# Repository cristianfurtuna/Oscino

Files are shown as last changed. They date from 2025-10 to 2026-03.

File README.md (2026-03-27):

# OSCINO - Osciloscop digital interfațat USB cu intrare izolată galvanic
Proiectul nostru constă într-un osciloscop digital interfațat prin USB, capabil să achiziționeze, să proceseze și să afișeze semnale electrice în timp real pe PC.
## Specificații
- in: 5V DC USB-C;<br>
- out: >2 Mbit/s serial UART data;<br>
- Arduino Mega compatible pinout
- sampling rate: ~300 ksa/s;<br>
- AC/DC coupling;<br>
- Galvanically Isolated Frontend with Differential Signal Aquisition;<br>
- 0...230V AC/DC input range using different attenuation stages;<br>
- Attenuator for High Input Voltages;<br>
- UI for PC use;<br>
- timebase and synchronisation (trigger).<br>
## Elaborare etape
- [x] Alegere componente<br>
- [x] Schemă electrică<br>
- [x] Cablaj<br>
- [x] Prototip<br>
- [x] Programare uC<br>
- [x] Programare UI<br>
- [x] Testare<br>
- [x] Elaborare documentație<br>
- [x] Realizare prezentare PowerPoint<br>
## Alegerea unui microcontroller potrivit
- [ ] C8051F120 -> preț: $11.22<br>
- [ ] STM32H743ZIT6 -> preț: $15.23<br>
- [ ] MIMXRT1062DVL6B -> preț: $12.00<br>
- [x] ATMEGA 2560 -> preț: $10.56<br>
## Asamblarea PCB-ului la fabrică este mult prea scumpă pentru a finaliza cablajul (TBD asamblare manuală)

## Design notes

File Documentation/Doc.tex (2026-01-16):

% !TeX program = lualatex
\documentclass[12pt,a4paper]{report}

% --------------------- PACKAGES ---------------------
\usepackage{fontspec}             % Custom font
\usepackage{pdfpages}             % Atach PDFs
\usepackage{graphicx}             % Images
\usepackage{amsmath,amssymb}      % Math
\usepackage{caption}              % Figure/table captions
\usepackage{subcaption}           % Subfigures
\usepackage{geometry}             % Margins
\usepackage{fancyhdr}             % Headers/footers
\usepackage{tocloft}              % ToC/List formatting
\usepackage[acronym,nonumberlist]{glossaries} % Acronyms
\usepackage[hidelinks]{hyperref}  % Hyperlinks
\usepackage{titlesec}             % Section title styling
\usepackage{listings}             % Source code
\usepackage{chngcntr}             % Counter tweaks
\usepackage{tabularx}             % Tables
\usepackage{tikz}                 % Graphs
\usepackage{pgfplots}             % Plots
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

\titleformat{\subsection}
{\normalfont\fontsize{12}{16}\bfseries\selectfont}
{\thesubsection}{16pt}{}
\titlespacing{\subsection}{1.25cm}{10pt}{0pt}

\renewcommand{\normalsize}{\fontsize{12}{16}\selectfont}

% ------- HEADER & FOOTER
\pagestyle{fancy}
\setlength{\headheight}{18pt}
\setlength{\footskip}{70pt}
\fancyhf{}
\fancyhead[L]{
	\ifodd\value{page}{\projecttitle}
	\else\makebox[0pt][l]{\parbox[b]{\headwidth}{\raggedleft{\studentname}}}
	\fi}
\fancyfoot[C]{\raisebox{15mm}{\thepage}}

\fancypagestyle{plain}{
	\fancyhf{}
	\fancyhead[L]{
		\ifodd\value{page}{\projecttitle}
		\else\makebox[0pt][l]{\parbox[b]{\headwidth}{\raggedleft{\studentname}}}
		\fi}
	\fancyfoot[C]{\raisebox{15mm}{\thepage}}
}

\fancypagestyle{plainfooter}{
	\fancyhf{}
	\renewcommand{\headrulewidth}{0pt}\setlength{\footskip}{70pt}
	\fancyfoot[C]{\raisebox{15mm}{\thepage}}
}

% --------------------- FIGURE, TABLE & CODE STYLES -----------------

% ------- TABLE OF CONTENTS
\renewcommand{\cftchapdotsep}{\cftdotsep}
\setlength{\cftchapnumwidth}{3em}
\renewcommand{\cftchapleader}{\cftdotfill{\cftchapdotsep}}
\AtBeginDocument{\renewcommand\contentsname{}}

% ------- BIBLIOGRAPHY
\defbibheading{bibliography}[\refname]{\chapter{Bibliografie}}
\renewcommand*{\bibfont}{\small}

% ------- FIGURES
\captionsetup{
	font=small,
	labelfont=bf,
	labelsep=period
}

\AtBeginDocument{
	\renewcommand{\figurename}{Figura}
	\counterwithout{figure}{chapter}
	\renewcommand{\listfigurename}{}
	\renewcommand{\cftfigpresnum}{Figura~}
	\renewcommand{\cftfigaftersnum}{.} 
	\settowidth{\cftfignumwidth}{Figură 100.} 
}

% For removing extra space in list of figures
% \makeatletter
% \def\@chapter[#1]#2{
	%   \ifnum\c@secnumdepth>\m@ne%
	%     \refstepcounter{chapter}
	%     \typeout{\@chapapp\space\thechapter.}
	%     \addcontentsline{toc}{chapter}{\protect\numberline{\thechapter}#1}
	%   \else \addcontentsline{toc}{chapter}{#1} \fi
	%   \chaptermark{#1}
	%   \addtocontents{lot}{\protect\addvspace{10\p@}}
	%   \if@twocolumn\@topnewpage[\@makechapterhead{#2}] 
	%   \else \@makechapterhead{#2} \@afterheading\fi}
% \makeatother

% ------- TABLES
\captionsetup[table]{
	justification=raggedleft,
	singlelinecheck=false
}

\AtBeginDocument{
	\counterwithout{table}{chapter}
	\renewcommand{\listtablename}{}
	\renewcommand{\cfttabpresnum}{Tabelul~}
	\renewcommand{\cfttabaftersnum}{.}
	\settowidth{\cfttabnumwidth}{Tabelul 100.}
	\renewcommand{\tablename}{Tabelul}
}

\newcolumntype{L}[1]{>{\raggedright\arraybackslash}p{#1}}
\newcolumntype{C}[1]{>{\centering\arraybackslash}m{#1}}

% For removing extra space in list of tables
% \makeatletter
% \def\@chapter[#1]#2{
	%   \ifnum\c@secnumdepth>\m@ne
	%     \refstepcounter{chapter}
	%     \typeout{\@chapapp\space\thechapter.}
	%     \addcontentsline{toc}{chapter}{\protect\numberline{\thechapter}#1}
	%   \else \addcontentsline{toc}{chapter}{#1} \fi
	%   \chaptermark{#1}
	%   \addtocontents{lot}{\protect\addvspace{0pt}}
	%   \if@twocolumn\@topnewpage[\@makechapterhead{#2}]
	%   \else\@makechapterhead{#2}\@afterheading\fi}
% \makeatother

% ------- SOURCE CODE
\lstset{
	basicstyle=\fontspec{Courier New}\fontsize{12}{9.6}\selectfont,
	numbers=left,
	numberstyle=\scriptsize,
	breaklines=true,
	captionpos=b,
	frame=none,
	showstringspaces=false,
	xleftmargin=0.6cm,
}

% --------------------- ACRONYMS ---------------------
% ------- ADD ALL ACRONYMS HERE - REFERENCE THEM IN TEXT WITH \gls{name}
\newacronym{aicors}{AICoRS}{Artificial Intelligence-enabled Hardware Cosmic Radiation Sensor for Space Applications}
\newacronym{bga}{BGA}{Ball Grid Array}
\newacronym{bram}{BRAM}{Block Random-Access Memory}
\newacronym{can}{CAN}{Controller Area Network}
\newacronym{cmos}{CMOS}{Complementary Metal–Oxide–Semiconductor}

% --------------------- DOCUMENT ---------------------
% ------- UPDATE HERE WITH CORRESPONDING VALUES - NAME & TITLE
\newcommand{\studentname}{Furtună Cristian și Iordache Denis-Ninel}
\newcommand{\projecttitle}{Osciloscop Digital cu Izolare Galvanica}

\begin{document}
	
	% ------- THIS DOCUMENT IS MADE SEPARATELY AND ADDED HERE
	% ------- NO NEED TO MODIFY HERE - JUST UNCOMMENT

	\includepdf[pages=-, pagecommand={\thispagestyle{empty}}] {Anexe/Prima pagina.pdf}

	% ------- THE FOLLOWING PAGES ARE AUTOMATED - NO NEED TO MODIFY
	\chapter*{Cuprins}
	\vspace{-8em}
	\tableofcontents
	\newpage
	
	\chapter {Specificații hardware}
	\section{Componente alese \\} 
	\section*{Integrate parte Analogică}
	\begin{itemize}
		\item AMC3330 -- Amplificator izolat de precizie, optimizat pentru masurarea tensiunii
		\item ADS8920BRGET -- Convertor Analog-Digital (ADC) tip SAR de inalta viteza
		\item THS4521IDGK -- Amplificator operational complet diferential  zgomot redus
		\item LTV-356T -- Optocuploare pentru izolarea galvanica a semnalelor
		\item REF5045AD -- Referinta de tensiune de precizie (4.5V) si deriva termica mica
		\item TS5A23159DGS -- Comutator analogic dual SPDT (Single Pole Double Throw)
		\item ADuM1401xRW -- Izolator digital cu 4 canale pentru liniile de date
	\end{itemize}
	
	\section*{Integrate Digitale si de Alimentare}
	\begin{itemize}
		\item TEA1-0505 -- Convertor DC/DC izolat de 1 Watt pentru alimentare și izolare galvanică
		\item TPS259571DSGR -- Siguranta electronica (eFuse) cu monitorizare si protectie
		\item ATMEGA2560-16AU -- Microcontroler principal pe 8 biti, familia AVR
		\item FT230XQ -- Circuit interfata punte USB la UART serial
		
	\end{itemize}
	\section{Specificații finale \\}
	
	\begin{itemize}
		\item Backwards compatibility cu Arduino IDE (maparea pinilor este realizată în stil Arduino Mega)
		\item Frecvență maximă a semnalului de măsurat circa 300kHz (în funcție de configurarea ADC-ului, limită impusă de amplificatorul de intrare)
		\item Alimentare unică prin USB-C de 5V
		\item Transfer de date prin USB-C (Max. 2Mb/s)
		\item Intrare BNC
		\item Cuplaj AC/DC
		\item Encodere digitale pentru control al afișajului (baza de timp și scară de tensiune)
		\item Tensiune semnal de intrare >230Vac
		\item Dublă izolare galvanică pe interfața de intrare a semnalelor.
		
	\end{itemize}
	
	\section{Design hardware și pcb}
	Ideea acestui proiect este să creeze o izolare galvanică între partea analogică și digitală și să măsoare diferențial tensiunile aplicate la intrare astfel încât să protejeze echipamentul cu care 
	
	\begin{figure}[h!]
		\centering
		
		\caption{Schema etajului de intrare.}%
		\label{fig:Intrare}
	\end{figure}
	
	\begin{figure}[h!]
		\centering
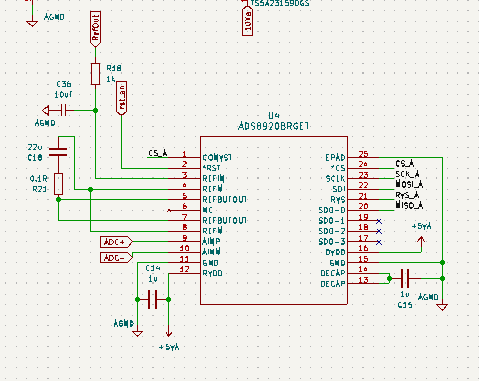
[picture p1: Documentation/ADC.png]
		
		\caption{Schema modulului ADC.}%
		\label{fig:ADC}
	\end{figure}
	
	\begin{figure}[h!]
		\centering
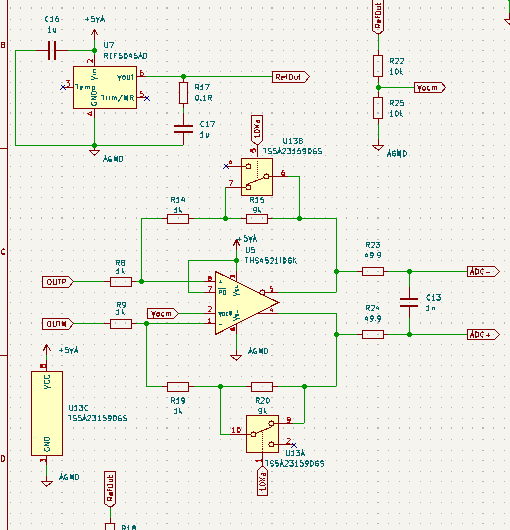
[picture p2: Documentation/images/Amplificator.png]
		
		\caption{Schema circuitului amplificator.}%
		\label{fig:Amplificator}
	\end{figure}
	
	\begin{figure}[h!]
		\centering
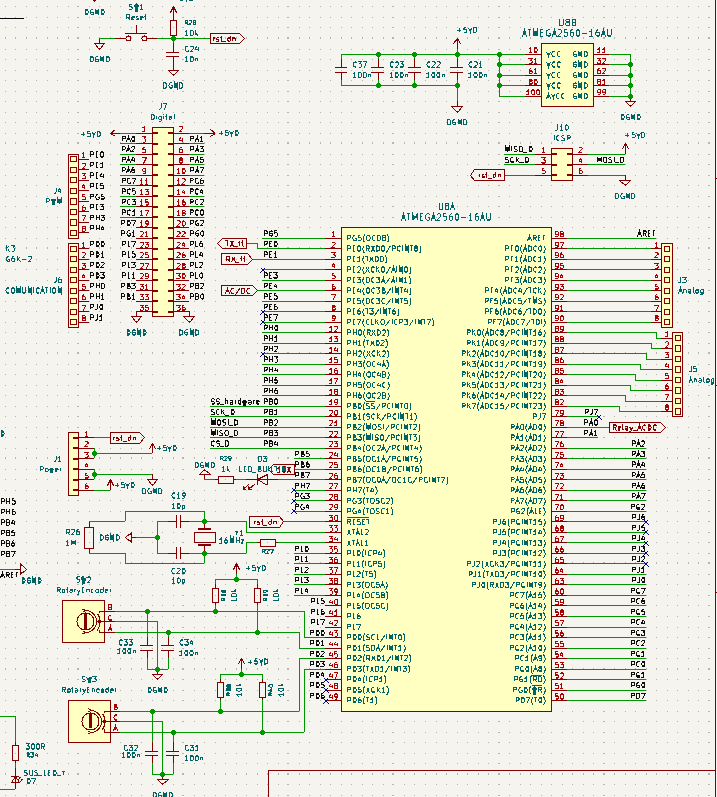
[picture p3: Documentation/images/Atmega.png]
		
		\caption{Configurația microcontrolerului ATmega.}%
		\label{fig:Atmega}
	\end{figure}

	\begin{figure}[h!]
		\centering
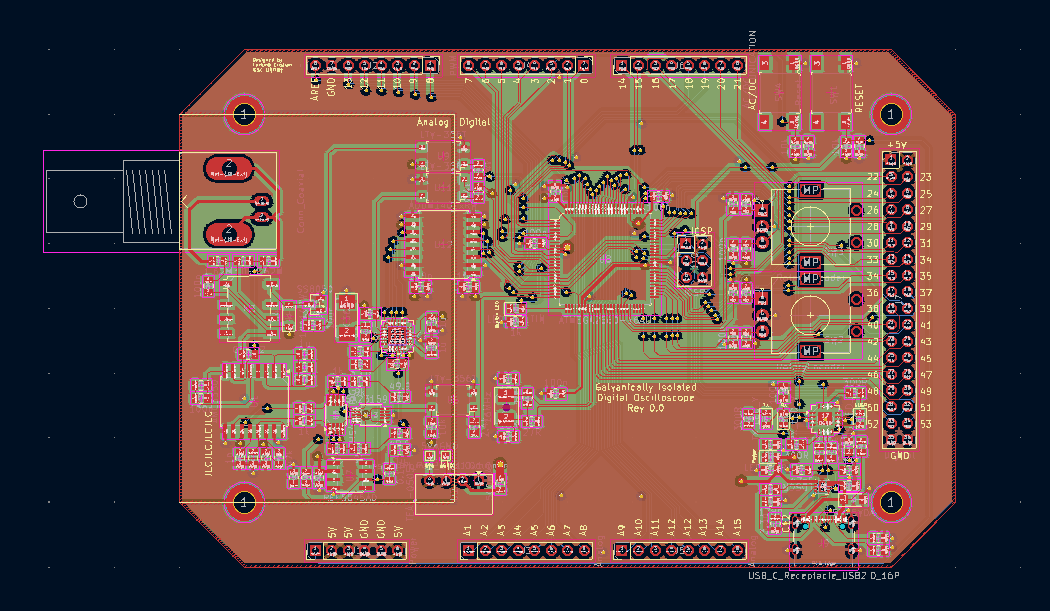
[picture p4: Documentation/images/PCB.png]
		
		\caption{Design-ul (layout-ul) plăcii PCB.}%
		\label{fig:PCB}
	\end{figure}

	\begin{figure}[h!]
		\centering
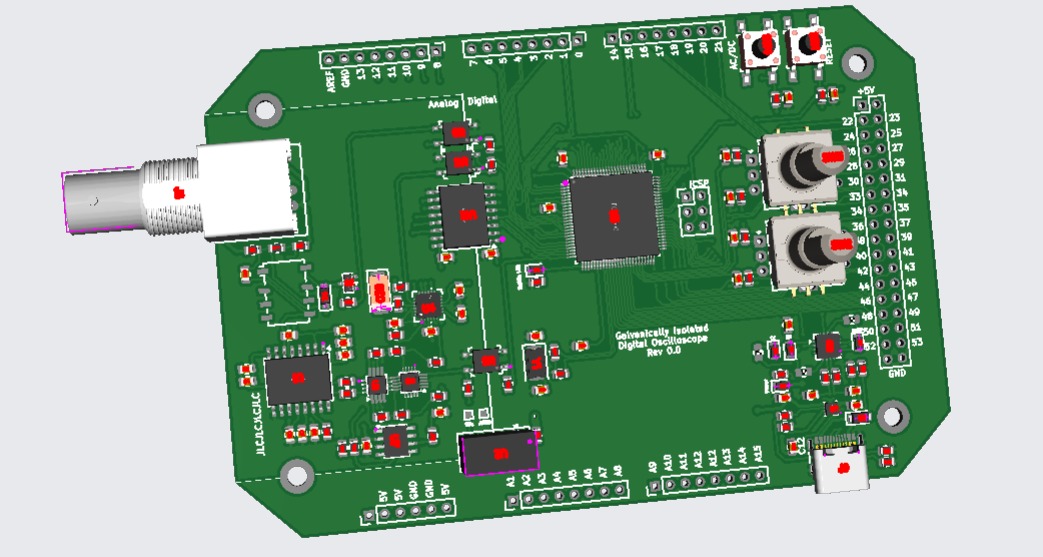
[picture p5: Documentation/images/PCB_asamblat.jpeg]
		
		\caption{Fotografie cu modulul PCB asamblat.}%
		\label{fig:PCB_asamblat}
	\end{figure}

	\section{Analiză economică}
	
	\begin{table}[h!]
		\begin{tabular}{|l|l|l|l|l|}
			\hline
			Cost PCB        & Cost PCBA                     & Cost estimativ componente & Cost estimativ minim & Cost prototip \\ 
			\hline
			$\sim$320 RON& $\sim$1300 RON & 300 + RON & 600 RON & 180 RON\\
			\hline

		\end{tabular}
	\end{table}
	
	Prin urmare, analizând cu atenție costurile din ofertele studiate, am decis să ne limităm la un PCB neasamblat + prototip realizat cu Arduino Mega 2560. Ne-am fi dorit să ne putem permite costul total de realizare a unui PCBA, dar cu măsurile de austeritate în vigoare, bursele tăiate pe perioada de vacanță și un trai tot mai scump de la o zi la alta, plus costurile de realizare a proiectului de licență, am considerat să ne oprim la o sumă totală de aprox. 500 de lei.
	
	\chapter {Specificații software}
	\section {Prototip}
	
	Așa cum a fost menționat și în secțiunea de \textbf{Analiză Economică}, pentru partea de simulare ne-am limitat la un prototip realizat cu o placă de dezvoltare Arduino Mega 2560.
	
	\begin{figure}[h!]
		\centering
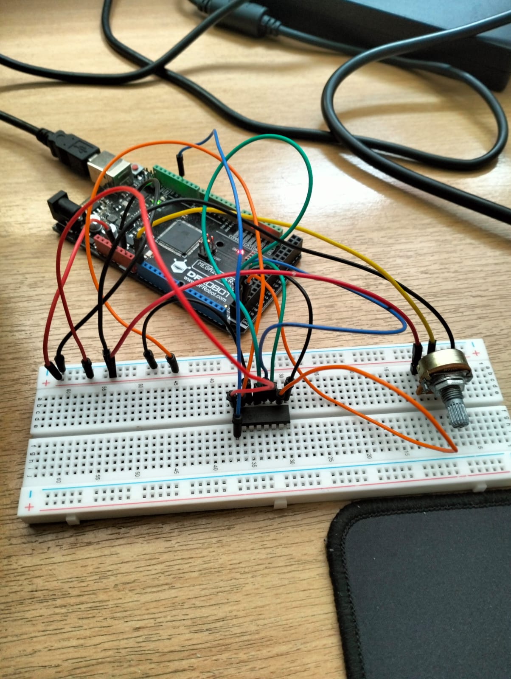
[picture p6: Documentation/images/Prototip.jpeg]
		
		\caption{Fotografie cu circuitul aferent prototipului nostru implementat pe un breadboard.}%
		\label{fig:Prototip}
	\end{figure}
	
	Pentru circuit a fost utilizat un ADC extern pe 10 biți, MCP3008 și un potențiometru pentru setarea factorului de umplere al unui semnal dreptunghiular generat pe pinul D11 al plăcii Arduino Mega 2560.
	
	Pinout-ul este evidențiat în următorul tabel:
	\begin{table}[h!]
		\centering
		\begin{tabular}{|c|c|c|}
			\hline
			Pin MCP3008        & Pin ATMEGA2560                     & Nume pini \\ 
			\hline
			1 & D11 & CH0-D11 \\
			\hline
			9 & DGND & DGND - DGND \\
			\hline
			10 & D53 & CS-SS \\
			\hline
			11 & D51 & DIN-MOSI \\
			\hline
			12 & D50 & DOUT-MISO \\
			\hline
			13 & D52 & CLK-SCK \\
			\hline
			14 & AGND & AGND-AGND \\
			\hline
			15 & 5V & VREF-5V \\
			\hline
			16 & 5V & VDD-5V \\
			\hline
		\end{tabular}
	\end{table}
	
	\section{Codul sursă utilizat}
	
	\begin{lstlisting}[language=C]
	#ifndef SPI_H
	#define SPI_H
	
	#include <avr/io.h>
	
	void SPI_MasterInit(void);
	uint8_t SPI_MasterTransmit(uint8_t data);
	void SPI_SlaveInit(void);
	uint8_t SPI_SlaveReceive(void);
	uint8_t SPI_Read_MCP3008_8bit(uint8_t channel);
	
	#endif
	\end{lstlisting}

	\begin{lstlisting}[language=C]
	#include <stdio.h>
	#include <avr/io.h>
	#include "spi.h"
	#include "uart.h"
	
	void SPI_MasterInit(void)
	{
		// Set MOSI, SS and SCK output, all others input
		DDRB |= (1 << PB2) | (1 << PB1) | (1 << PB0); // MOSI - PB2, SCK - PB1
		// Enable SPI, Master, set clock rate fck/16 (was 1 << SPR0)
		PORTB |= (1 << PB0);                           // Keep board in Master mode
		SPCR = (1 << SPE) | (1 << MSTR) | (1 << SPR0); // SPCR - SPI control register
		SPSR |= (1 << SPI2X);
	}
	
	uint8_t SPI_MasterTransmit(uint8_t data)
	{
		// Start transmission; load byte into data register
		SPDR = data; // SPDR - SPI data register
		// Wait for transmission to complete
		while (!(SPSR & (1 << SPIF)))
		;        // SPSR - SPI status register ; SPIF - SPI Interrupt Flag
		return SPDR; // read received byte after transmission
	}
	
	void SPI_SlaveInit(void)
	{
		// SET MISO output, all others input
		DDRB |= (1 << PB3); // MISO - PB3
		// Enable SPI
		SPCR = (1 << SPE); // SPCR - SPI control register
	}
	
	uint8_t SPI_SlaveReceive(void)
	{
		// Wait for reception complete
		while (!(SPSR & (1 << SPIF)))
		;        // SPSR - SPI status register ; SPIF - SPI Interrupt Flag
		return SPDR; // SPDR - SPI data register
	}
	
	// Read data from ADC
	uint8_t SPI_Read_MCP3008_8bit(uint8_t channel)
	{
		// CS Low
		PORTB &= ~(1 << PB0);
		
		// Send Start Bit (0x01)
		SPDR = 0x01;
		while (!(SPSR & (1 << SPIF)))
		;
		
		// Send config bit and select channel
		SPDR = 0x80 | (channel << 4);
		while (!(SPSR & (1 << SPIF)))
		;
		uint8_t high = SPDR;
		
		// Send dummy bit
		SPDR = 0x00;
		while (!(SPSR & (1 << SPIF)))
		;
		uint8_t low = SPDR;
		
		// CS High
		PORTB |= (1 << PB0);
		
		// Concatenam high si low
		uint16_t result = ((high & 0x03) << 8) | low;
		// Shiftare la dreapta pentru a pastra doar 1 byte
		// La frecvente mari, de regula ultimii 2 biti sunt zgomotosi
		return (uint8_t)(result >> 2);
	}
	\end{lstlisting}
	
	\begin{lstlisting}[language=C]
		#define BAUD 2000000UL // desired BAUD rate
		
		#include <avr/io.h>
		#include <avr/interrupt.h>
		#include <util/delay.h>
		#include <stdio.h>
		#include <stdint.h>
		#include "uart.h"
		#include "gpio.h"
		#include "avr/portpins.h"
		#include "pwm.h"
		#include "avr/sleep.h"
		#include "millis.h"
		#include "adc.h"
		#include "spi.h"
		
		#define PWM_FREQ 200 // Hz
		#define BATCH_SIZE 600
		
		volatile uint8_t button_pressed = 1;
		
		int main(void)
		{
			
			GPIO_set_output(ONBOARD_LED); // onboard LED
			GPIO_set_output(D11);		  // D11 as output
			
			uart_init(MYUBRR);
			SPI_MasterInit();
			millis_init();
			
			// Generate a square signal on pin D11
			PWM_init();
			PWM_attach(D11);
			ADC_init(ADC_REF_AVCC, ADC_PRESCALER_128);
			
			set_sleep_mode(SLEEP_MODE_IDLE); // Set sleep mode to power down
			
			EICRA |= (1 << ISC00); // Any logical change on INT0 generates interrupt
			EIMSK |= (1 << INT0);  // Enable INT0
			sei();				   // Enable global interrupts
			
			while (1)
			{
				// Modify duty cycle of pwm with a potentiometer
				static uint32_t last_pwm_update = 0;
				
				if (millis_now() - last_pwm_update >= 50)
				{
					uint16_t pot = ADC_read_pin(A0); // 0–1023
					uint32_t duty = (uint32_t)pot * PWM_get_max(D11) / 1023;
					
					PWM_write_raw(D11, duty); // hardware PWM
					last_pwm_update = millis_now();
				}
				
				cli(); // clear interrupts for full focus on sending ADC data
				// Send batch sync bytes 0xAA start byte, 0x55 stop byte, useful for python script
				while (!(UCSR0A & (1 << UDRE0)))
				;
				UDR0 = 0xAA;
				while (!(UCSR0A & (1 << UDRE0)))
				;
				UDR0 = 0x55;
				
				// Sending BATCH_SIZE = 600 bytes; total number of bits sent = estimated 6000 bits per for
				// Adding the start and stop bits to a byte -> 10 bits per batch
				// 6020 if we take into consideration the sync bytes for a batch
				for (uint16_t i = 0; i < BATCH_SIZE; i++)
				{
					// Read channel 0 from ADC
					uint8_t val = SPI_Read_MCP3008_8bit(0);
					
					// Send byte through UART
					while (!(UCSR0A & (1 << UDRE0)))
					;		// Wait for buffer to empty
					UDR0 = val; // Send the data
				}
				
				sei(); // enable interrupts
				_delay_us(100);
			}
		}
	\end{lstlisting}
	
	\begin{lstlisting}[language=Python]
		import sys
		import time
		import serial
		import numpy as np
		from numpy.lib.stride_tricks import sliding_window_view
		from PyQt5.QtWidgets import (
		QApplication, QMainWindow, QWidget, QVBoxLayout, QHBoxLayout,
		QLabel, QLineEdit, QPushButton, QDial, QGridLayout, QFrame, QGroupBox
		)
		from PyQt5.QtCore import QThread, pyqtSignal, Qt
		import pyqtgraph as pg
		
		# Constants
		SYNC_SEQ = b"\xAA\x55" # Sync bytes
		BATCH_SIZE = 600 # Size of ADC data batch
		ADC_REF_VOLTAGE = 5.0  # Reference voltage of ADC = VDD (5V)
		
		# Step values for volts/div and timescale
		TIME_STEPS = [0.0001, 0.0002, 0.0005, 0.001, 0.002, 0.005, 0.010, 0.020, 0.050, 0.100]
		VOLT_STEPS = [0.1, 0.2, 0.5, 1.0, 2.0, 5.0]
		
		class SerialADCReader:
		# Configure port, baud rate and timeout
		def __init__(self, port="COM5", baudrate=2000000):
		self.ser = serial.Serial(port, baudrate, timeout=0.01)
		self.rx_buf = bytearray() # Internal buffer for received data
		
		# Open the port
		def connect(self):
		if not self.ser.is_open:
		self.ser.open()
		self.ser.reset_input_buffer() # Reset internal buffer to get rid of junk data from previous runs
		
		# Close the port
		def disconnect(self):
		if self.ser.is_open:
		self.ser.close()
		
		def read_frame(self):
		# Read everything on the serial buffer
		if self.ser.in_waiting > 0:
		data = self.ser.read(self.ser.in_waiting)
		self.rx_buf.extend(data) # Add everything from the serial buffer into our internal buffer for further processing
		
		frames_found = []
		while True:
		# Search the buffer for Sync bits to find a batch
		idx = self.rx_buf.find(SYNC_SEQ)
		# If there are no Sync bits found and the buffer has grown in size too much
		# Clear the buffer and keep only the last 100 bytes
		if idx == -1:
		if len(self.rx_buf) > 2 * BATCH_SIZE:
		self.rx_buf = self.rx_buf[-100:] 
		break
		
		# Verify if there are enough bytes for a full batch
		# If there are not, wait for full batch
		pkt_len = 2 + BATCH_SIZE # 2 bytes Sync + batch size
		if len(self.rx_buf) < idx + pkt_len:
		break 
		
		payload = self.rx_buf[idx + 2 : idx + pkt_len] # Skip sync bytes and extract only the necessary data
		raw_data = np.frombuffer(payload, dtype=np.uint8) # Convert into decimal values (0-255 for 8 bits)
		# Scale the values into (0 - 1020) to simulate 10 bit ADC
		# Added so I don't have to modify my program (previously used to send all 10 bits of ADC data)
		scaled_data = raw_data.astype(np.int16) * 4
		frames_found.extend(scaled_data)
		del self.rx_buf[:idx + pkt_len]
		
		return frames_found if frames_found else None
		
		# Preluare date din interfata seriala pe un thread separat, fara sa blochez GUI-ul
		class SerialThread(QThread):
		samples_ready = pyqtSignal(object) # Anunta programul principal ca am citit un batch pentru display
		
		# Initializare citire buffer serial
		def __init__(self, port):
		super().__init__()
		self.port = port
		self.running = False
		self.reader = None
		
		def run(self):
		try:
		self.reader = SerialADCReader(self.port)
		self.reader.connect()
		self.running = True
		#In timp ce citesc datele, daca am un frame complet, il trimit catre programul principal pentru prelucrare
		while self.running:
		samples = self.reader.read_frame()
		if samples:
		self.samples_ready.emit(samples)
		else:
		self.msleep(1) # Mic delay daca inca nu au aparut date ca sa nu blocam thread-ul inutil
		except Exception as e:
		print(f"Serial Error: {e}")  #In caz de eroare pe serial read
		finally:
		if self.reader:
		self.reader.disconnect() # Inchidere port serial (cu sau fara eroare)
		
		def stop(self):
		self.running = False
		self.wait()
		
		class MainWindow(QMainWindow):
		def __init__(self):
		super().__init__()
		
		self.serial_thread = None
		
		# Buffer circular
		self.capture_buffer = []
		self.MAX_CAPTURE = 500000 # Buffer mare
		
		# Variabile interne
		self.measured_sps = 60000.0 # Valoare default pana la masura
		self.total_samples_received = 0
		self.last_time_check = time.time()
		
		# Scope state
		self.time_idx = 4   # Default 2ms (index 4 in TIME_STEPS)
		self.volt_idx = 3   # Default 1V (index 3 in VOLT_STEPS)
		self.trigger_lvl = 2.5
		self.vert_offset = 0.0
		
		self.last_draw_time = 0
		self.FPS_LIMIT = 30  
		self.last_valid_frame = None 
		self.trigger_lost_timer = 0
		
		self._setup_ui()
		self._setup_plot()
		self.update_scope_settings() # Apply initial settings
		
		def _setup_ui(self):
		# Styling dial buttons
		dial_style = """
		QDial { background-color: #333; }
		"""
		
		# Zona de conectare
		self.port_input = QLineEdit("COM5") 
		self.port_input.setFixedWidth(80)
		self.btn_connect = QPushButton("ON")
		self.btn_connect.setCheckable(True)
		self.btn_connect.clicked.connect(self.toggle_connection)
		self.btn_connect.setStyleSheet("QPushButton { background-color: #444; color: white; border-radius: 5px; font-weight: bold; } QPushButton:checked { background-color: #00E676; color: black; }")
		self.btn_connect.setFixedSize(50, 50)
		
		conn_group = QGroupBox("Input")
		conn_layout = QVBoxLayout()
		conn_layout.addWidget(QLabel("PORT"))
		conn_layout.addWidget(self.port_input)
		conn_layout.addWidget(self.btn_connect)
		conn_layout.addStretch()
		conn_group.setLayout(conn_layout)
		
		# Zona Verticala (Volts/Div & Position - offset)
		self.dial_volts = QDial()
		self.dial_volts.setRange(0, len(VOLT_STEPS)-1)
		self.dial_volts.setValue(self.volt_idx)
		self.dial_volts.setNotchesVisible(True)
		self.dial_volts.valueChanged.connect(self.update_scope_settings)
		self.lbl_volts = QLabel("1 V")
		self.lbl_volts.setAlignment(Qt.AlignCenter)
		
		self.dial_offset = QDial()
		self.dial_offset.setRange(-60, 60) # +/- 6.0 Diviziuni
		self.dial_offset.setValue(0)
		self.dial_offset.setNotchesVisible(True)
		self.dial_offset.valueChanged.connect(self.update_scope_settings)
		self.lbl_offset = QLabel("Pos: 0 Div")
		self.lbl_offset.setAlignment(Qt.AlignCenter)
		
		vert_group = QGroupBox("Vertical")
		vert_layout = QVBoxLayout()
		vert_layout.addWidget(QLabel("SCALE"))
		vert_layout.addWidget(self.dial_volts)
		vert_layout.addWidget(self.lbl_volts)
		vert_layout.addWidget(QLabel("POSITION"))
		vert_layout.addWidget(self.dial_offset)
		vert_layout.addWidget(self.lbl_offset)
		vert_group.setLayout(vert_layout)
		
		# Zona Orizontală (Time/Div)
		self.dial_time = QDial()
		self.dial_time.setRange(0, len(TIME_STEPS)-1)
		self.dial_time.setValue(self.time_idx)
		self.dial_time.setNotchesVisible(True)
		self.dial_time.valueChanged.connect(self.update_scope_settings)
		self.lbl_time = QLabel("2 ms")
		self.lbl_time.setAlignment(Qt.AlignCenter)
		
		horiz_group = QGroupBox("Horizontal")
		horiz_layout = QVBoxLayout()
		horiz_layout.addWidget(QLabel("TIME/DIV"))
		horiz_layout.addWidget(self.dial_time)
		horiz_layout.addWidget(self.lbl_time)
		horiz_layout.addStretch()
		horiz_group.setLayout(horiz_layout)
		
		# Zona Trigger
		self.dial_trig = QDial()
		self.dial_trig.setRange(0, 50) # 0.0 la 5.0V
		self.dial_trig.setValue(25)
		self.dial_trig.setNotchesVisible(True)
		self.dial_trig.valueChanged.connect(self.update_scope_settings)
		self.lbl_trig_val = QLabel("T: 2.5V")
		self.lbl_trig_val.setAlignment(Qt.AlignCenter)
		
		self.lbl_trig_status = QLabel("NO SIG")
		self.lbl_trig_status.setStyleSheet("color: gray; font-weight: bold; border: 1px solid gray; padding: 2px;")
		self.lbl_trig_status.setAlignment(Qt.AlignCenter)
		
		trig_group = QGroupBox("Trigger")
		trig_layout = QVBoxLayout()
		trig_layout.addWidget(QLabel("LEVEL"))
		trig_layout.addWidget(self.dial_trig)
		trig_layout.addWidget(self.lbl_trig_val)
		trig_layout.addWidget(self.lbl_trig_status)
		trig_group.setLayout(trig_layout)
		
		# Panou Control (stanga)
		ctrl_layout = QVBoxLayout()
		ctrl_layout.addWidget(conn_group)
		ctrl_layout.addWidget(vert_group)
		ctrl_layout.addWidget(horiz_group)
		ctrl_layout.addWidget(trig_group)
		ctrl_layout.addStretch()
		
		ctrl_widget = QWidget()
		ctrl_widget.setLayout(ctrl_layout)
		ctrl_widget.setFixedWidth(180) # Latime fixa a panoului
		
		# Plot Area
		self.plot_widget = pg.GraphicsLayoutWidget()
		self.plot_widget.setBackground('#111') # Background inchis
		self.plot = self.plot_widget.addPlot(title="NIBIRUSCOPE")
		self.curve = self.plot.plot(pen=pg.mkPen('#00E676', width=2)) 
		
		# Setup Grid
		self.plot.showGrid(x=True, y=True, alpha=0.3)
		self.plot.setLabel('bottom', 'Time', units='s')
		self.plot.setLabel('left', 'Voltage', units='V')
		
		# Main Layout
		main_layout = QHBoxLayout()
		main_layout.addWidget(ctrl_widget)
		main_layout.addWidget(self.plot_widget)
		
		container = QWidget()
		container.setLayout(main_layout)
		self.setCentralWidget(container)
		self.setWindowTitle("NibiruScope")
		self.resize(1200, 700)
		
		def _setup_plot(self):
		pg.setConfigOptions(antialias=False) 
		
		def update_scope_settings(self):
		# Timebase
		idx_t = self.dial_time.value()
		time_val = TIME_STEPS[idx_t]
		
		if time_val < 0.001:
		self.lbl_time.setText(f"{time_val*1000000:.0f} µs")
		elif time_val < 1.0:
		self.lbl_time.setText(f"{time_val*1000:.0f} ms")
		else:
		self.lbl_time.setText(f"{time_val:.2f} s")
		
		# Volts/div
		idx_v = self.dial_volts.value()
		volt_per_div = VOLT_STEPS[idx_v]
		self.lbl_volts.setText(f"{volt_per_div} V")
		
		# Position - Offset
		# Modifica valoarea dial-ului in diviziuni
		offset_in_divs = self.dial_offset.value() / 10.0
		
		# Scalare pentru diferite valori de volts/div
		self.vert_offset = offset_in_divs * volt_per_div 
		
		# Afisare label offset scalat in volti pentru dial
		self.lbl_offset.setText(f"Pos: {self.vert_offset:+.1f}V")
		
		# Trigger
		trig_raw = self.dial_trig.value()
		self.trigger_lvl = trig_raw / 10.0
		self.lbl_trig_val.setText(f"T: {self.trigger_lvl:.1f}V")

		# Axa X
		self.plot.setXRange(0, time_val * 10, padding=0)
		
		# Axa Y:
		half_screen_volts = volt_per_div * 4 
		self.plot.setYRange(-half_screen_volts, half_screen_volts, padding=0)
		
		# Functionalitate on/off
		def toggle_connection(self):
		if self.btn_connect.isChecked():
		port = self.port_input.text()
		self.serial_thread = SerialThread(port)
		self.serial_thread.samples_ready.connect(self.process_data)
		self.serial_thread.start()
		self.btn_connect.setText("OFF")
		else:
		if self.serial_thread:
		self.serial_thread.stop()
		self.serial_thread = None
		self.btn_connect.setText("ON")
		
		def process_data(self, samples):
		self.total_samples_received += len(samples)
		now = time.time()
		if now - self.last_time_check >= 1.0:
		self.measured_sps = self.total_samples_received / (now - self.last_time_check)
		self.total_samples_received = 0
		self.last_time_check = now
		# Actualizăm titlul ferestrei
		# self.plot.setTitle(f"NIBIRU SCOPE - Sampling: {self.measured_sps/1000:.1f} kSPS")
		
		# Buffer Management
		self.capture_buffer.extend(samples)
		if len(self.capture_buffer) > self.MAX_CAPTURE:
		self.capture_buffer = self.capture_buffer[-self.MAX_CAPTURE:]
		
		# Limitare FPS
		if now - self.last_draw_time < (1.0 / self.FPS_LIMIT):
		return

		time_per_div = TIME_STEPS[self.dial_time.value()]
		total_time_screen = time_per_div * 10
		
		n_display_points = int(total_time_screen * self.measured_sps)
		
		n_display_points = max(10, min(n_display_points, len(self.capture_buffer)))
		
		if len(self.capture_buffer) < n_display_points * 2:
		return
		
		# Procesare date
		# Luăm un chunk mare din coadă pentru a căuta trigger-ul
		# Luăm dublu cât ne trebuie ca să avem loc de manevră
		search_window = int(n_display_points * 2.5) 
		if search_window > len(self.capture_buffer):
		search_window = len(self.capture_buffer)
		
		raw_data = np.array(self.capture_buffer[-search_window:], dtype=np.int16)
		
		# Filtru Median (doar dacă avem destule puncte)
		if len(raw_data) > 5:
		window = sliding_window_view(raw_data, window_shape=3)
		filtered_data = np.median(window, axis=1)
		else:
		filtered_data = raw_data
		
		# --- 6. TRIGGER LOGIC ---
		trig_adc = int((self.trigger_lvl / 5.0) * 1023)
		
		# Cautare rising edge
		binary = (filtered_data >= trig_adc).astype(np.int8)
		edges = np.diff(binary)
		trigger_indices = np.where(edges == 1)[0]
		
		frame_to_draw = None
		found_trigger = False
		
		if len(trigger_indices) > 0:
		
		for idx in reversed(trigger_indices):
		if idx + n_display_points < len(filtered_data):
		if np.all(filtered_data[idx+1 : idx+4] > (trig_adc - 20)):
		frame_to_draw = filtered_data[idx : idx + n_display_points]
		found_trigger = True
		
		self.lbl_trig_status.setText("LOCKED")
		self.lbl_trig_status.setStyleSheet("color: #00E676; border: 1px solid #00E676; font-weight: bold;")
		self.trigger_lost_timer = now
		break
		
		# Auto roll
		if not found_trigger:
		if now - self.trigger_lost_timer > 0.3: 
		self.lbl_trig_status.setText("AUTO")
		self.lbl_trig_status.setStyleSheet("color: orange; border: 1px solid orange;")
		# Luam ultimele date disponibile
		if len(filtered_data) >= n_display_points:
		frame_to_draw = filtered_data[-n_display_points:]
		
		# Desenare
		if frame_to_draw is not None:
		self.last_draw_time = now
		
		# Conversie in Volti
		real_volts = (frame_to_draw / 1023.0) * 5.0
		
		display_volts = (real_volts - 2.5) + self.vert_offset
		
		# Generare axa timp
		total_time_screen = time_per_div * 10
		t = np.linspace(0, total_time_screen, len(display_volts))
		
		self.curve.setData(t, display_volts)
		
		if __name__ == "__main__":
		app = QApplication(sys.argv)
		window = MainWindow()
		window.show()
		sys.exit(app.exec_())
	\end{lstlisting}

	% ------- THESE DOCUMENTS ARE MADE SEPARATELY AND ADDED HERE
	% ------- NO NEED TO MODIFY HERE - JUST UNCOMMENT
	% \newpage
	% \addcontentsline{toc}{chapter}{Anexa 1}
	% \includepdf[pages=-, pagecommand={\thispagestyle{plainfooter}}]
	% {Anexe/Anexa 1.pdf}
	
	% \newpage
	% \addcontentsline{toc}{chapter}{Anexa 2} 
	% \includepdf[pages=-, pagecommand={\thispagestyle{plainfooter}}]
	% {Anexe/Anexa 2.pdf}
	
	% \newpage
	% \addcontentsline{toc}{chapter}{Anexa 3}
	% \includepdf[pages=-, pagecommand={\thispagestyle{plainfooter}}]
	% {Anexe/Anexa 3.pdf}
	
	% \newpage
	% \addcontentsline{toc}{chapter}{Declarație privind originalitatea}
	% \includepdf[pages=-, pagecommand={\thispagestyle{plainfooter}}]
	% {Anexe/Declaratie originalitate.pdf}
	
\end{document}

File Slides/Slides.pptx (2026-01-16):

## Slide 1

NIBIRU
Osciloscop Digital cu Izolație Galvanică

Furtună Cristian
Iordache Denis-Ninel

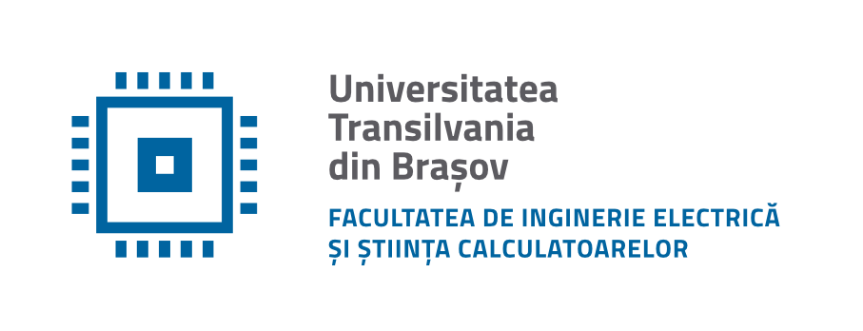
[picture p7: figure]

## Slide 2

Schematic

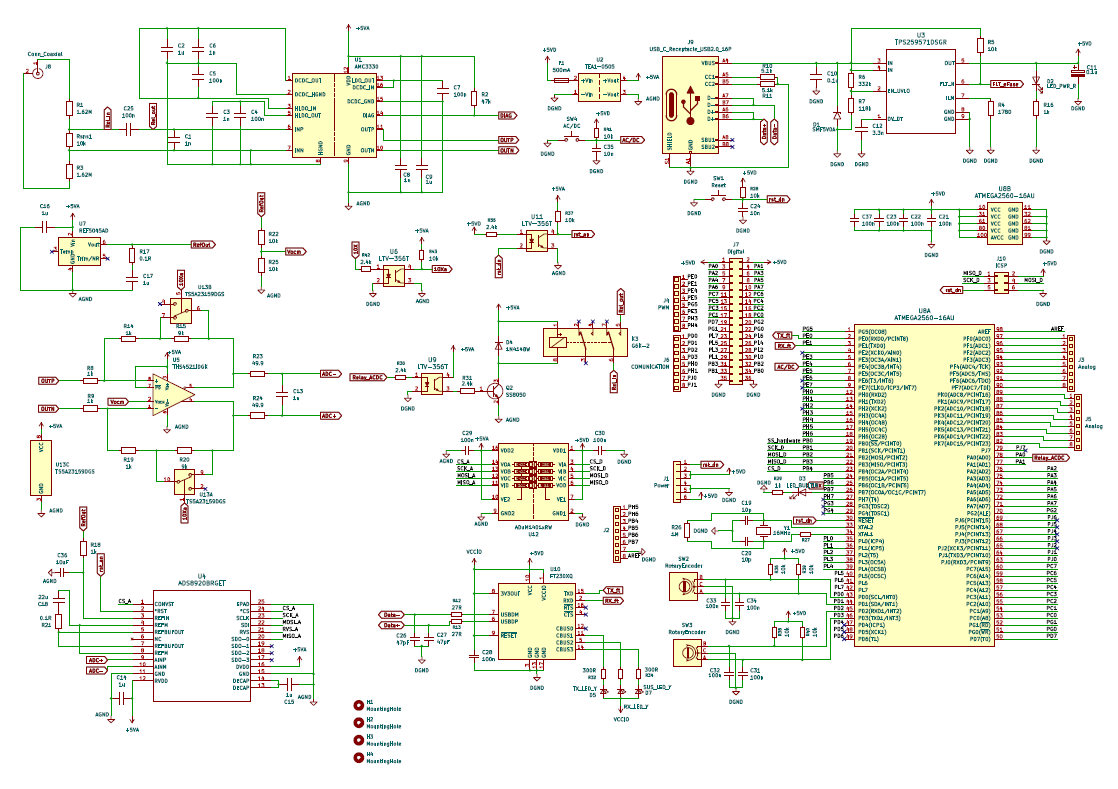
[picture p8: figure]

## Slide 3

PCB Design

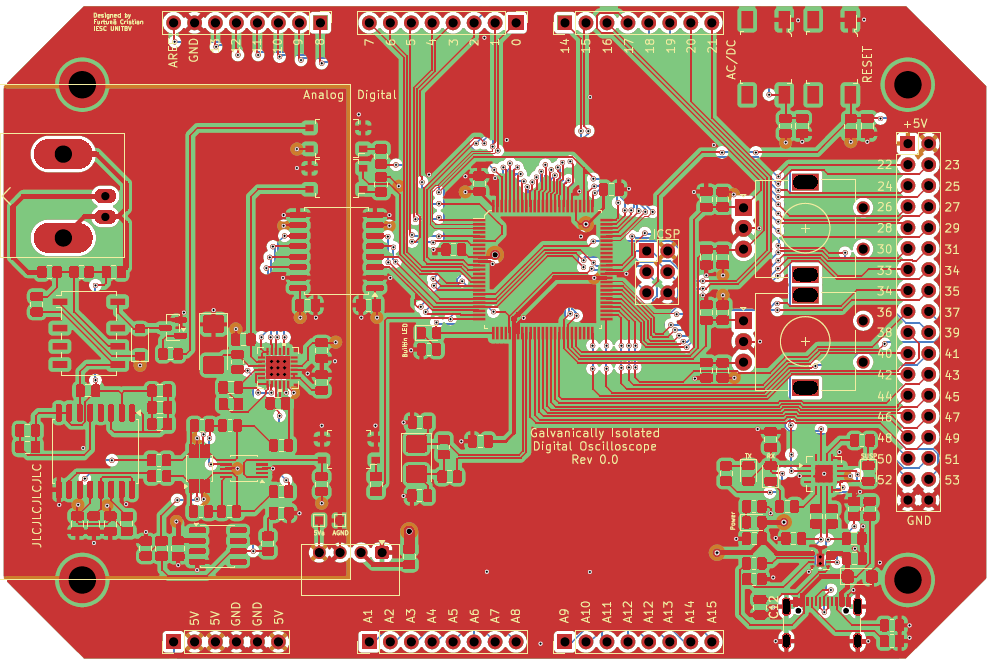
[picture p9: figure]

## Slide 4

PCB Design Bottom

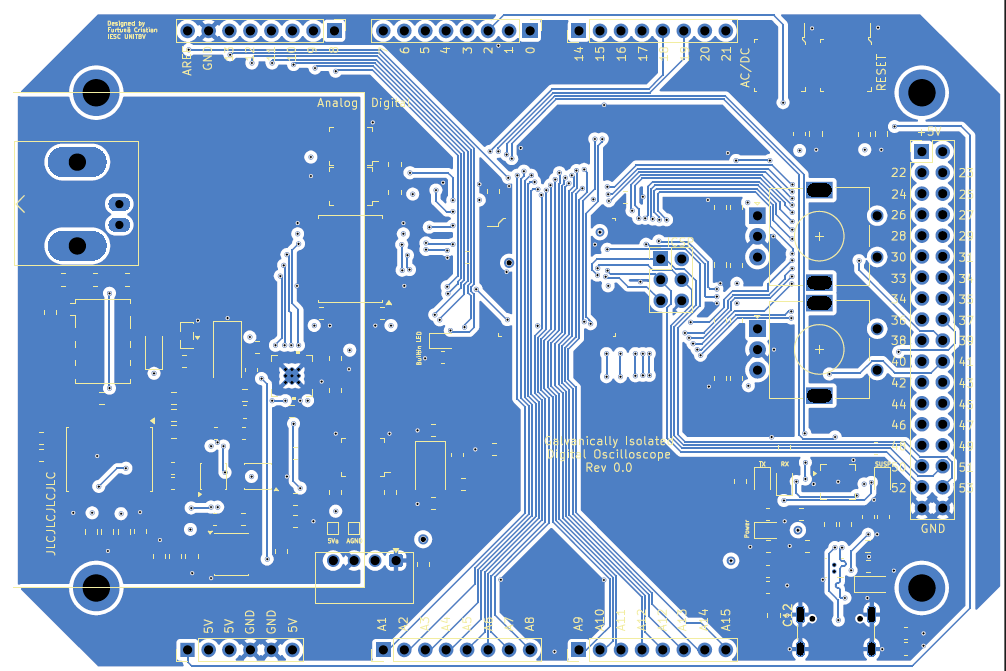
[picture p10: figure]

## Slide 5

PCB Design 3D

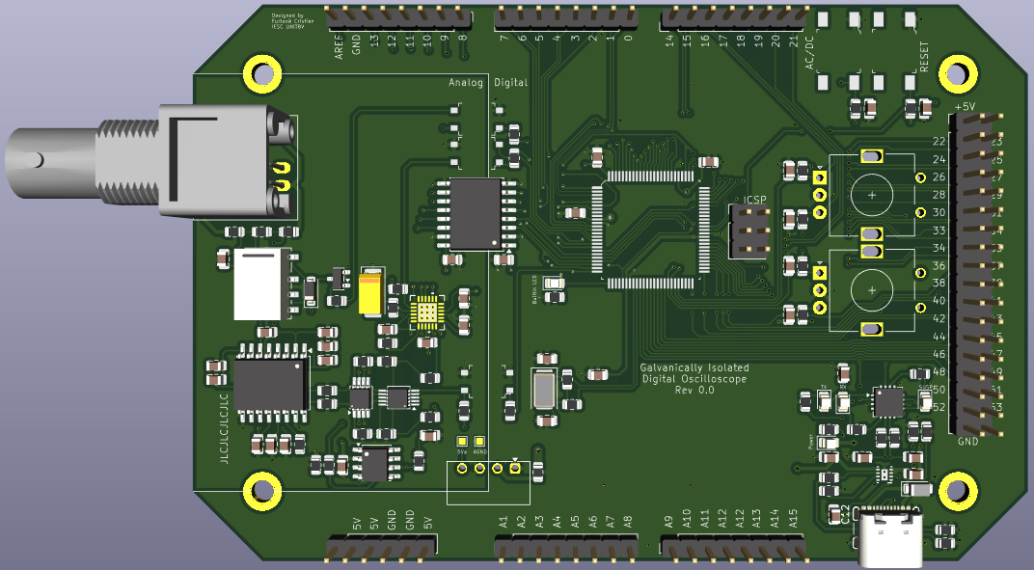
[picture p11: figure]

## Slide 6

Specificații hardware finale

• Backwards compatibility cu Arduino IDE (maparea pinilor este realizată în stil Arduino Mega)
• Frecvență maximă a semnalului de măsurat circa 300kHz (în funcție de configurarea ADC-ului, limită impusă de amplificatorul de intrare)
• Alimentare unică prin USB-C de 5V
• Transfer de date prin USB-C (Max. 2Mb/s)
• Intrare BNC
• Cuplaj AC/DC
• Encodere digitale pentru control al afișajului (baza de timp și scară de tensiune)

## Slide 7

Specificații hardware finale

• Modularitate hardware și software, posibilitatea de reconfigurare a oricărui parametru și de adăugare a unor funcționalități noi prin pinii GPIO
• Consum energetic estimativ maxim mai mic de 2W
• Circuit de protecție la scurtcircuit la alimentare (e-Fuse)
• Comunicație digitală izolată prin izolatori cu cuplaj inductiv și optocuploare
• ADC cu aproximări succesive configurabil

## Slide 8

Specificații software

• Prototip realizat cu placă de dezvoltare Arduino Mega 2560 și ADC extern pe 10 biți MCP3008.
• Comunicare cu ADC-ul extern realizată prin SPI.
• Trimitere date seriale prin UART pentru afișare pe GUI realizat în Python.
• Semnal de test PWM cu duty cycle configurabil generat cu Arduino Mega 2560.
• GUI similar unui osciloscop real, funcționalități de trigger, modificare volt/div (SCALE), modificare timebase, poziționare semnal pe ecran.

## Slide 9

GUI Demo

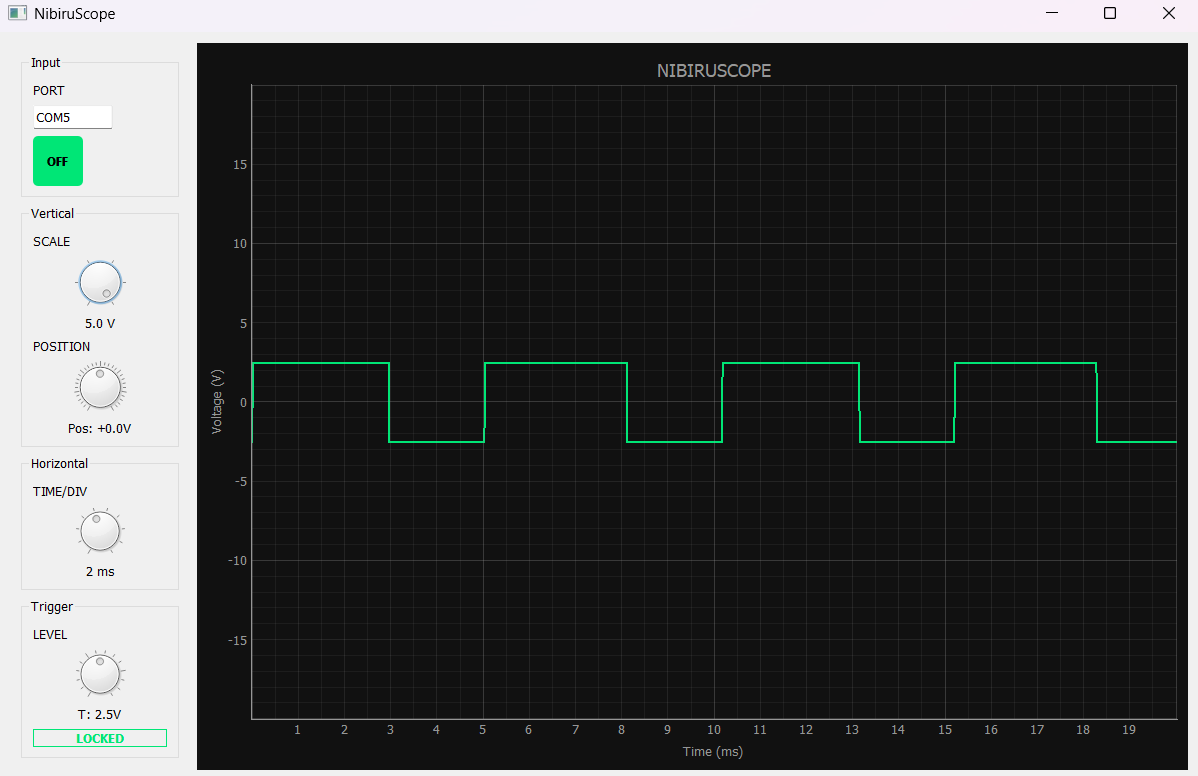
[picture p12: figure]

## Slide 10

GUI Demo

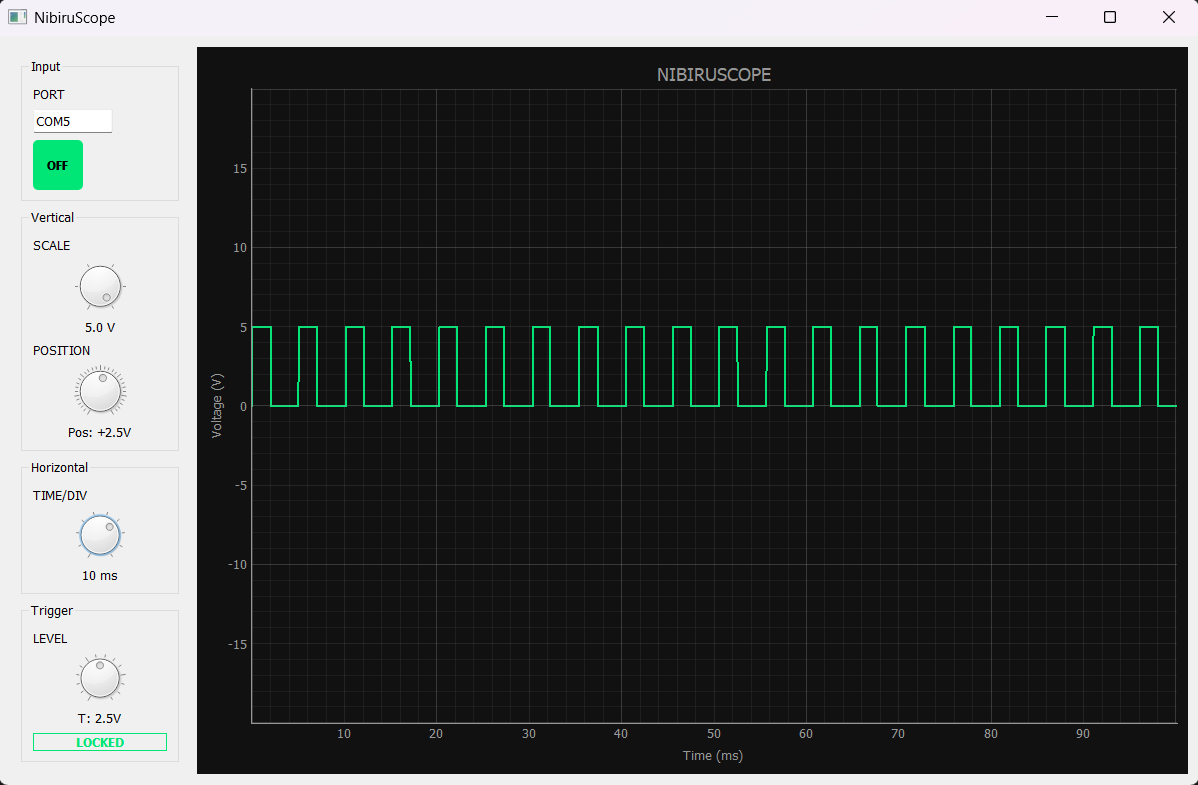
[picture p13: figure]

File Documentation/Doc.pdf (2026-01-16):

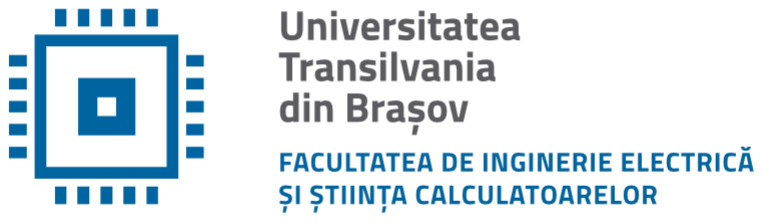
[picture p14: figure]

# Documentație APM

# Prof. Coordonator: S. L. KERTESZ CSABA ZOLTAN Furtună Cristian Iordache Denis-Ninel

# BRAȘOV, 2026

# Furtună Cristian și Iordache Denis-Ninel

# CUPRINS

# 1 Specificații hardware | 3 1.1 Componente alese

| 3

# 1.2 Specificații finale

| 3

# 1.3 Design hardware și pcb | 4 1.4 Analiză economică | 4

# 2 Specificații software | 9 2.1 Prototip | 9 2.2 Codul sursă utilizat | 10

# Osciloscop Digital cu Izolare Galvanica

# 1 SPECIFICAȚII HARDWARE

# 1.1 COMPONENTE ALESE

# INTEGRATE PARTE ANALOGICĂ

# - AMC3330 – Amplificator izolat de precizie, optimizat pentru masurarea tensiunii

# - ADS8920BRGET – Convertor Analog-Digital (ADC) tip SAR de inalta viteza

# - THS4521IDGK – Amplificator operational complet diferential zgomot redus

# - LTV-356T – Optocuploare pentru izolarea galvanica a semnalelor

# - REF5045AD – Referinta de tensiune de precizie (4.5V) si deriva termica mica

# - TS5A23159DGS – Comutator analogic dual SPDT (Single Pole Double Throw)

# - ADuM1401xRW – Izolator digital cu 4 canale pentru liniile de date

# INTEGRATE DIGITALE SI DE ALIMENTARE

# - TEA1-0505 – Convertor DC/DC izolat de 1 Watt pentru alimentare și izolare galvanică

# - TPS259571DSGR – Siguranta electronica (eFuse) cu monitorizare si protectie

# - ATMEGA2560-16AU – Microcontroler principal pe 8 biti, familia AVR

# - FT230XQ – Circuit interfata punte USB la UART serial

# 1.2 SPECIFICAȚII FINALE

- Backwards compatibility cu Arduino IDE (maparea pinilor este realizată în stil Arduino Mega)

# - Frecvență maximă a semnalului de măsurat circa 300kHz (în funcție de configurarea ADC-ului, limită impusă de amplificatorul de intrare)

# - Alimentare unică prin USB-C de 5V

# - Transfer de date prin USB-C (Max. 2Mb/s)

# - Intrare BNC

# - Cuplaj AC/DC

# - Encodere digitale pentru control al afișajului (baza de timp și scară de tensiune)

# - Tensiune semnal de intrare >230Vac

- Dublă izolare galvanică pe interfața de intrare a semnalelor.

# 1.3 DESIGN HARDWARE ȘI PCB

Ideea acestui proiect este să creeze o izolare galvanică între partea analogică și digitală și să măsoare diferențial tensiunile aplicate la intrare astfel încât să protejeze echipamentul cu care

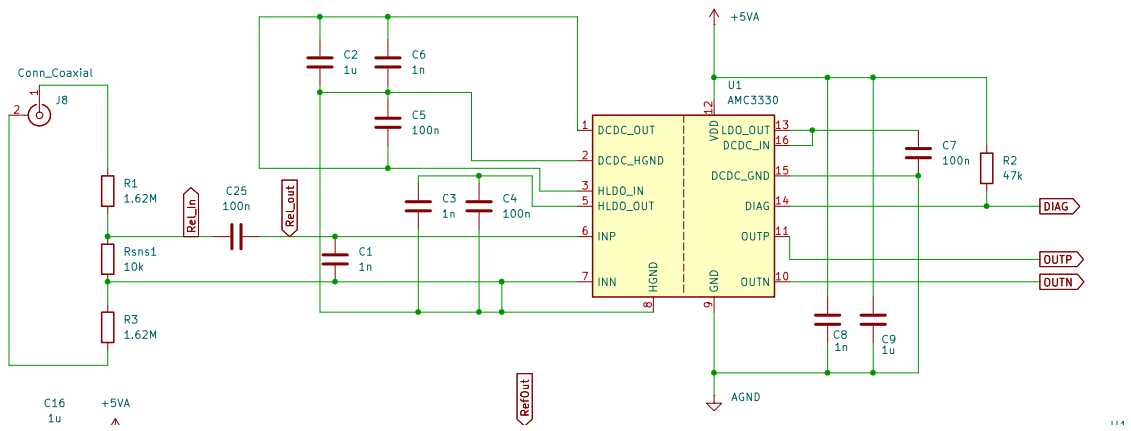
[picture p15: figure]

Figura 1. Schema etajului de intrare.

# 1.4 ANALIZĂ ECONOMICĂ

Cost PCB | Cost PCBA | Cost estimativ componente | Cost estimativ minim | Cost prototip
∼320 RON | ∼1300 RON | 300 + RON | 600 RON | 180 RON

Prin urmare, analizând cu atenție costurile din ofertele studiate, am decis să ne limităm la un PCB neasamblat + prototip realizat cu Arduino Mega 2560. Ne-am fi dorit să ne putem permite costul total de realizare a unui PCBA, dar cu măsurile de austeritate în vigoare, bursele tăiate pe perioada de vacanță și un trai tot mai scump de la o zi la alta, plus costurile de realizare a proiectului de licență, am considerat să ne oprim la o sumă totală de aprox. 500 de lei.


Figura 2. Schema modulului ADC.


Figura 3. Schema circuitului amplificator.


Figura 4. Configurația microcontrolerului ATmega.

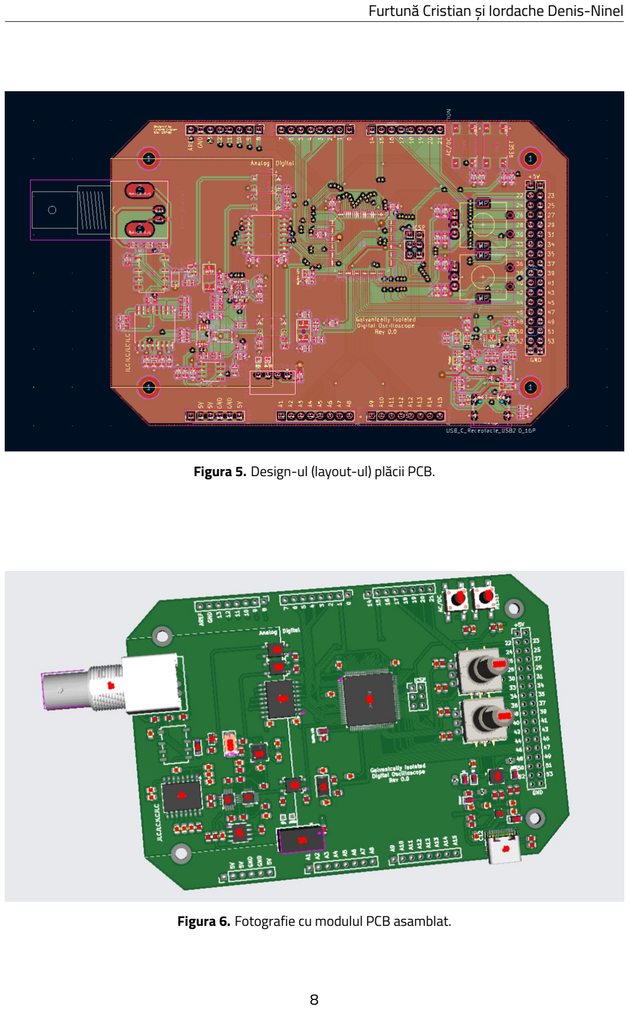
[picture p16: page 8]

Figura 5. Design-ul (layout-ul) plăcii PCB.

Figura 6. Fotografie cu modulul PCB asamblat.

# 2 SPECIFICAȚII SOFTWARE

# 2.1 PROTOTIP

# Așa cum a fost menționat și în secțiunea de Analiză Economică, pentru partea de simulare

ne-am limitat la un prototip realizat cu o placă de dezvoltare Arduino Mega 2560.

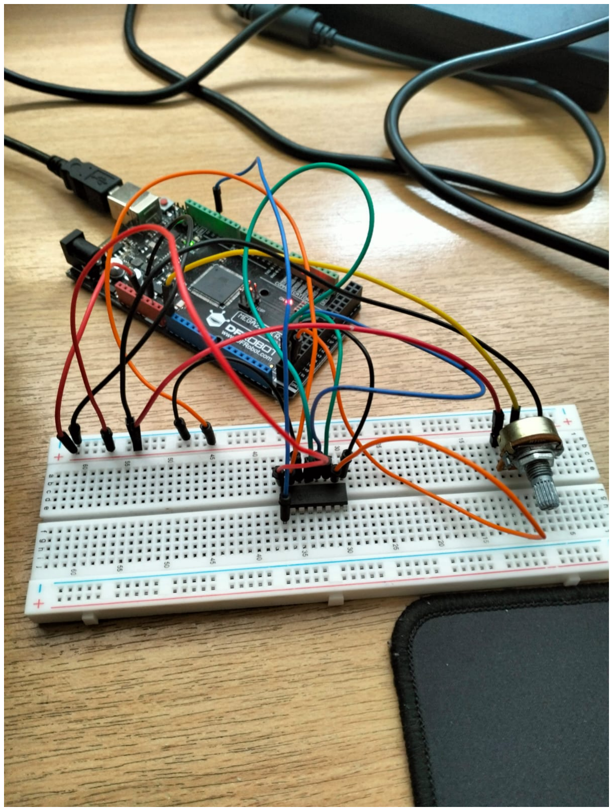
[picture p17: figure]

Figura 7. Fotografie cu circuitul aferent prototipului nostru implementat pe un breadboard.

Pentru circuit a fost utilizat un ADC extern pe 10 biți, MCP3008 și un potențiometru pentru setarea factorului de umplere al unui semnal dreptunghiular generat pe pinul D11 al plăcii Arduino Mega 2560.

# Pinout-ul este evidențiat în următorul tabel:

Pin MCP3008 | Pin ATMEGA2560 | Nume pini
1 | D11 | CH0-D11
9 | DGND | DGND - DGND
10 | D53 | CS-SS
11 | D51 | DIN-MOSI
12 | D50 | DOUT-MISO
13 | D52 | CLK-SCK
14 | AGND | AGND-AGND
15 | 5V | VREF-5V
16 | 5V | VDD-5V

# 2.2 CODUL SURSĂ UTILIZAT

1 | #ifndef SPI_H
2 | #define SPI_H
3
4 | #include <avr/io.h>
5
6 | void SPI_MasterInit(void);
7 | uint8_t SPI_MasterTransmit(uint8_t data);
8 | void SPI_SlaveInit(void);
9 | uint8_t SPI_SlaveReceive(void);
10 | uint8_t SPI_Read_MCP3008_8bit(uint8_t channel);
11
12 | #endif
1 | #include <stdio.h>
2 | #include <avr/io.h>
3 | #include "spi.h"
4 | #include "uart.h"
5
6 | void SPI_MasterInit(void)
7 | {
8 | // Set MOSI, SS and SCK output, all others input
9 | DDRB |= (1 << PB2) | (1 << PB1) | (1 << PB0); //
| | MOSI − PB2, SCK − PB1
10 | // Enable SPI, Master, set clock rate fck/16 (
| | was 1 << SPR0)
11 | PORTB |= (1 << PB0);
| | // Keep board in Master mode
12 | SPCR = (1 << SPE) | (1 << MSTR) | (1 << SPR0);
| | // SPCR − SPI control register
13 | SPSR |= (1 << SPI2X);
14 | }
15
16 | uint8_t SPI_MasterTransmit(uint8_t data)
17 | {
18 | // Start transmission; load byte into data
| | register
19 | SPDR = data; // SPDR − SPI data register
20 | // Wait for transmission to complete
21 | while (!(SPSR & (1 << SPIF)))
22 | ; | // SPSR − SPI status register ; SPIF −
| | SPI Interrupt Flag
23 | return SPDR; // read received byte after
| | transmission

}

void SPI_SlaveInit(void)
{
// SET MISO output, all others input DDRB |= (1 << PB3); // MISO − PB3
// Enable SPI
SPCR = (1 << SPE); // SPCR − SPI control register
}

uint8_t SPI_SlaveReceive(void) {
// Wait for reception complete while (!(SPSR & (1 << SPIF)))
38 | ; | // SPSR − SPI status register ; SPIF − SPI Interrupt Flag

return SPDR; // SPDR − SPI data register }

// Read data from ADC
uint8_t SPI_Read_MCP3008_8bit(uint8_t channel) {
// CS Low
PORTB &= ~(1 << PB0);

// Send Start Bit (0x01)
SPDR = 0x01;
while (!(SPSR & (1 << SPIF)))
;

// Send config bit and select channel
SPDR = 0x80 | (channel << 4);
while (!(SPSR & (1 << SPIF)))
;
uint8_t high = SPDR;

// Send dummy bit
SPDR = 0x00;
while (!(SPSR & (1 << SPIF))) ;
uint8_t low = SPDR;

// CS High
PORTB |= (1 << PB0);

// Concatenam high si low
uint16_t result = ((high & 0x03) << 8) | low;
// Shiftare la dreapta pentru a pastra doar 1 byte
// La frecvente mari, de regula ultimii 2 biti
| | sunt zgomotosi
return (uint8_t)(result >> 2);
}

#define BAUD 2000000UL // desired BAUD rate

#include <avr/io.h>

#include <avr/interrupt.h>

#include <util/delay.h>

6 | #include <stdio.h> 7 | #include <stdint.h> 8 | #include "uart.h" 9 | #include "gpio.h"
10 | #include "avr/portpins.h"
11 | #include "pwm.h"
12 | #include "avr/sleep.h"
13 | #include "millis.h"
14 | #include "adc.h"
15 | #include "spi.h"
16
17 | #define PWM_FREQ 200 // Hz
18 | #define BATCH_SIZE 600
19
20 | volatile uint8_t button_pressed = 1;
21
22 | int main(void )
23
{
24
25 | GPIO_set_output(ONBOARD_LED); // onboard
| LED
26 | GPIO_set_output(D11); | // D11
| as output
27
28 | uart_init(MYUBRR);
29 | SPI_MasterInit();
30 | millis_init();
31
32 | // Generate a square signal on pin D11
33 | PWM_init();
34 | PWM_attach(D11);
35 | ADC_init(ADC_REF_AVCC, ADC_PRESCALER_128
| );
36
37 | set_sleep_mode(SLEEP_MODE_IDLE); // Set
sleep mode to power down
38
39 | EICRA |= (1 << ISC00); // Any logical
change on INT0 generates interrupt
40 | EIMSK |= (1 << INT0); | // Enable INT0
41 | sei(); | //
Enable global interrupts
42
43 | while (1)
44
| {
45 | // Modify duty cycle of pwm with
a potentiometer
46 | static uint32_t last_pwm_update
| = 0;
47
48 | if (millis_now() −
last_pwm_update >= 50)
49
| {
50 | uint16_t pot =
ADC_read_pin(A0); // –01023
51 | uint32_t duty = (
uint32_t)pot
*
PWM_get_max(D11) /
1023;

52
53 | PWM_write_raw(D11, duty)
; // hardware PWM
54 | last_pwm_update =
millis_now();
55 | }
56
57 | cli(); // clear interrupts for
full focus on sending ADC data
58 | // Send batch sync bytes 0xAA
start byte, 0x55 stop byte, useful for python script
59 | while (!(UCSR0A & (1 << UDRE0)))
60 | ;
61 | UDR0 = 0xAA;
62 | while (!(UCSR0A & (1 << UDRE0)))
63 | ;
64 | UDR0 = 0x55;
65
66 | // Sending BATCH_SIZE = 600
bytes; total number of bits sent = estimated 6000 bits per for
67 | // Adding the start and stop
bits to a byte −> 10 bits per batch
68 | // 6020 if we take into
consideration the sync bytes
| for a batch
69 | for (uint16_t i = 0; i <
| BATCH_SIZE; i++)
70 | {
71 | // Read channel 0 from
ADC
72 | uint8_t val =
| | SPI_Read_MCP3008_8bit
(0);
73
74 | // Send byte through
UART
75 | while (!(UCSR0A & (1 <<
UDRE0)))
76 | ; | // Wait
| | for buffer to empty
77 | UDR0 = val; // Send the
data
78 | }
79
80 | sei(); // enable interrupts
81 | _delay_us(100);
82 | }
83 | }
1 | import sys
2 | import time
3 | import serial
4 | import numpy as np
5 | from numpy.lib.stride_tricks import
sliding_window_view
6 | from PyQt5.QtWidgets import (
7 | QApplication, QMainWindow, QWidget, QVBoxLayout,

QHBoxLayout,
QLabel, QLineEdit, QPushButton, QDial, QGridLayout, QFrame, QGroupBox
)
from PyQt5.QtCore import QThread, pyqtSignal, Qt import pyqtgraph as pg

# Constants

SYNC_SEQ = b"\xAA\x55" # Sync bytes
BATCH_SIZE = 600 # Size of ADC data batch
16 | ADC_REF_VOLTAGE = 5.0 | # Reference voltage of
| ADC = VDD (5V)

# Step values for volts/div and timescale TIME_STEPS = [0.0001, 0.0002, 0.0005, 0.001, 0.002, 0.005, 0.010, 0.020, 0.050, 0.100] VOLT_STEPS = [0.1, 0.2, 0.5, 1.0, 2.0, 5.0]

| class SerialADCReader:
# Configure port, baud rate and timeout

def __init__(self, port="COM5", baudrate
| =2000000):
self.ser = serial.Serial(port, baudrate, timeout
| =0.01)
self.rx_buf = bytearray() # Internal buffer for
| received data
| # Open the port def connect(self):

if not self.ser.is_open:
| self.ser.open()
self.ser.reset_input_buffer() # Reset internal buffer to get rid of junk data from previous
| runs
| # Close the port def disconnect(self): if self.ser.is_open: self.ser.close()
| def read_frame(self):
# Read everything on the serial buffer

if self.ser.in_waiting > 0:
data = self.ser.read(self.ser.in_waiting) self.rx_buf.extend(data) # Add everything from the serial buffer into our internal buffer for
| further processing
| frames_found = [] while True:

# Search the buffer for Sync bits to find a

| batch
idx = self.rx_buf.find(SYNC_SEQ)
# If there are no Sync bits found and the buffer has grown in size too much

# Clear the buffer and keep only the last 100

| bytes if idx == −1: if len(self.rx_buf) > 2 | * BATCH_SIZE:

self.rx_buf = self.rx_buf[−100:]
| break

# Verify if there are enough bytes for a full batch

# If there are not, wait for full batch pkt_len = 2 + BATCH_SIZE # 2 bytes Sync + batch size

if len(self.rx_buf) < idx + pkt_len:
break

payload = self.rx_buf[idx + 2 : idx + pkt_len] # Skip sync bytes and extract only the necessary data
raw_data = np.frombuffer(payload, dtype=np.uint8 ) # Convert into decimal values (0−255 for 8 bits)
# Scale the values into (0 − 1020) to simulate 10 bit ADC

# Added so I don't have to modify my program ( previously used to send all 10 bits of ADC data)

scaled_data = raw_data.astype(np.int16) * 4 frames_found.extend(scaled_data)
del self.rx_buf[:idx + pkt_len]

return frames_found if frames_found else None

# Preluare date din interfata seriala pe un thread separat, fara sa blochez GUI−ul class SerialThread(QThread):

samples_ready = pyqtSignal(object) # Anunta programul principal ca am citit un batch pentru display

# Initializare citire buffer serial

def __init__(self, port):
super().__init__()
self.port = port
self.running = False
self.reader = None

def run(self):
try:
self.reader = SerialADCReader(self.port) self.reader.connect()
self.running = True
#In timp ce citesc datele, daca am un frame complet, il trimit catre programul principal pentru prelucrare

while self.running:
samples = self.reader.read_frame()
if samples:
self.samples_ready.emit(samples)
else:
self.msleep(1) # Mic delay daca inca nu au aparut date ca sa nu blocam thread−ul inutil except Exception as e:
96 | print(f"Serial Error: {e}") | #In caz de eroare
| pe serial read finally:
| if self.reader:
self.reader.disconnect() # Inchidere port serial
| (cu sau fara eroare)

101 | def stop(self):
102 | self.running = False
103 | self.wait()
104
105 | class MainWindow(QMainWindow):
106 | def __init__(self):
107 | super().__init__()
108
109 | self.serial_thread = None
110
111 | # Buffer circular
112 | self.capture_buffer = []
113 | self.MAX_CAPTURE = 500000 # Buffer mare
114
115 | # Variabile interne
116 | self.measured_sps = 60000.0 # Valoare default
| pana la masura
117 | self.total_samples_received = 0
118 | self.last_time_check = time.time()
119
120 | # Scope state
121 | self.time_idx = 4 | # Default 2ms (index 4 in
| TIME_STEPS)
122 | self.volt_idx = 3 | # Default 1V (index 3 in
| VOLT_STEPS)
123 | self.trigger_lvl = 2.5
124 | self.vert_offset = 0.0
125
126 | self.last_draw_time = 0
127 | self.FPS_LIMIT = 30
128 | self.last_valid_frame = None
129 | self.trigger_lost_timer = 0
130
131 | self._setup_ui()
132 | self._setup_plot()
133 | self.update_scope_settings() # Apply initial
| settings
134
135 | def _setup_ui(self):
136 | # Styling dial buttons
137 | dial_style = """
138 | QDial { background−color: #333; }
139 | """
140
141 | # Zona de conectare
142 | self.port_input = QLineEdit("COM5")
143 | self.port_input.setFixedWidth(80)
144 | self.btn_connect = QPushButton("ON")
145 | self.btn_connect.setCheckable(True)
146 | self.btn_connect.clicked.connect(self.
toggle_connection)
147 | self.btn_connect.setStyleSheet("QPushButton {
background−color: #444; color: white; border− radius: 5px; font−weight: bold; } QPushButton: checked { background−color: #00E676; color:
| black; }")
148 | self.btn_connect.setFixedSize(50, 50)
149
150 | conn_group = QGroupBox("Input")
151 | conn_layout = QVBoxLayout()
152 | conn_layout.addWidget(QLabel("PORT"))
153 | conn_layout.addWidget(self.port_input)

154 | conn_layout.addWidget(self.btn_connect)
155 | conn_layout.addStretch()
156 | conn_group.setLayout(conn_layout)
157
158 | # Zona Verticala (Volts/Div & Position − offset)
159 | self.dial_volts = QDial()
160 | self.dial_volts.setRange(0, len(VOLT_STEPS)−1)
161 | self.dial_volts.setValue(self.volt_idx)
162 | self.dial_volts.setNotchesVisible(True)
163 | self.dial_volts.valueChanged.connect(self.
| update_scope_settings)
164 | self.lbl_volts = QLabel("1 V")
165 | self.lbl_volts.setAlignment(Qt.AlignCenter)
166
167 | self.dial_offset = QDial()
168 | self.dial_offset.setRange(−60, 60) # +/− 6.0
| Diviziuni
169 | self.dial_offset.setValue(0)
170 | self.dial_offset.setNotchesVisible(True)
171 | self.dial_offset.valueChanged.connect(self.
| update_scope_settings)
172 | self.lbl_offset = QLabel("Pos: 0 Div")
173 | self.lbl_offset.setAlignment(Qt.AlignCenter)
174
175 | vert_group = QGroupBox("Vertical")
176 | vert_layout = QVBoxLayout()
177 | vert_layout.addWidget(QLabel("SCALE"))
178 | vert_layout.addWidget(self.dial_volts)
179 | vert_layout.addWidget(self.lbl_volts)
180 | vert_layout.addWidget(QLabel("POSITION"))
181 | vert_layout.addWidget(self.dial_offset)
182 | vert_layout.addWidget(self.lbl_offset)
183 | vert_group.setLayout(vert_layout)
184
185 | # Zona ăOrizontal (Time/Div)
186 | self.dial_time = QDial()
187 | self.dial_time.setRange(0, len(TIME_STEPS)−1)
188 | self.dial_time.setValue(self.time_idx)
189 | self.dial_time.setNotchesVisible(True)
190 | self.dial_time.valueChanged.connect(self.
| update_scope_settings)
191 | self.lbl_time = QLabel("2 ms")
192 | self.lbl_time.setAlignment(Qt.AlignCenter)
193
194 | horiz_group = QGroupBox("Horizontal")
195 | horiz_layout = QVBoxLayout()
196 | horiz_layout.addWidget(QLabel("TIME/DIV"))
197 | horiz_layout.addWidget(self.dial_time)
198 | horiz_layout.addWidget(self.lbl_time)
199 | horiz_layout.addStretch()
200 | horiz_group.setLayout(horiz_layout)
201
202 | # Zona Trigger
203 | self.dial_trig = QDial()
204 | self.dial_trig.setRange(0, 50) # 0.0 la 5.0V
205 | self.dial_trig.setValue(25)
206 | self.dial_trig.setNotchesVisible(True)
207 | self.dial_trig.valueChanged.connect(self.
| update_scope_settings)
208 | self.lbl_trig_val = QLabel("T: 2.5V")
209 | self.lbl_trig_val.setAlignment(Qt.AlignCenter)

210
211 | self.lbl_trig_status = QLabel("NO SIG")
212 | self.lbl_trig_status.setStyleSheet("color: gray;
| font−weight: bold; border: 1px solid gray;
| padding: 2px;")
213 | self.lbl_trig_status.setAlignment(Qt.AlignCenter )

214
215 | trig_group = QGroupBox("Trigger")
216 | trig_layout = QVBoxLayout()
217 | trig_layout.addWidget(QLabel("LEVEL"))
218 | trig_layout.addWidget(self.dial_trig)
219 | trig_layout.addWidget(self.lbl_trig_val)
220 | trig_layout.addWidget(self.lbl_trig_status)
221 | trig_group.setLayout(trig_layout)
222
223 | # Panou Control (stanga)
224 | ctrl_layout = QVBoxLayout()
225 | ctrl_layout.addWidget(conn_group)
226 | ctrl_layout.addWidget(vert_group)
227 | ctrl_layout.addWidget(horiz_group)
228 | ctrl_layout.addWidget(trig_group)
229 | ctrl_layout.addStretch()
230
231 | ctrl_widget = QWidget()
232 | ctrl_widget.setLayout(ctrl_layout)
233 | ctrl_widget.setFixedWidth(180) # Latime fixa a
| panoului
234
235 | # Plot Area
236 | self.plot_widget = pg.GraphicsLayoutWidget()
237 | self.plot_widget.setBackground('#111') #
| Background inchis
238 | self.plot = self.plot_widget.addPlot(title="
| NIBIRUSCOPE")
239 | self.curve = self.plot.plot(pen=pg.mkPen('#00
| E676', width=2))
240
241 | # Setup Grid
242 | self.plot.showGrid(x=True, y=True, alpha=0.3)
243 | self.plot.setLabel('bottom', 'Time', units='s')
244 | self.plot.setLabel('left', 'Voltage', units='V')
245
246 | # Main Layout
247 | main_layout = QHBoxLayout()
248 | main_layout.addWidget(ctrl_widget)
249 | main_layout.addWidget(self.plot_widget)
250
251 | container = QWidget()
252 | container.setLayout(main_layout)
253 | self.setCentralWidget(container)
254 | self.setWindowTitle("NibiruScope")
255 | self.resize(1200, 700)
256
257 | def _setup_plot(self):
258 | pg.setConfigOptions(antialias=False)
259
260 | def update_scope_settings(self):
261 | # Timebase
262 | idx_t = self.dial_time.value()
263 | time_val = TIME_STEPS[idx_t]

if time_val < 0.001:
self.lbl_time.setText(f"{time_val*¹⁰⁰⁰⁰⁰⁰:.0f} µs")
elif time_val < 1.0:
self.lbl_time.setText(f"{time_val*¹⁰⁰⁰:.0f} ms") else:
self.lbl_time.setText(f"{time_val:.2f} s")

# Volts/div

idx_v = self.dial_volts.value() volt_per_div = VOLT_STEPS[idx_v] self.lbl_volts.setText(f"{volt_per_div} V")

# Position − Offset

# Modifica valoarea dial−ului in diviziuni offset_in_divs = self.dial_offset.value() / 10.0

# Scalare pentru diferite valori de volts/div self.vert_offset = offset_in_divs * volt_per_div

# Afisare label offset scalat in volti pentru dial

self.lbl_offset.setText(f"Pos: {self.vert_offset :+.1f}V")

# Trigger

trig_raw = self.dial_trig.value() self.trigger_lvl = trig_raw / 10.0 self.lbl_trig_val.setText(f"T: {self.trigger_lvl :.1f}V")

# Axa X

self.plot.setXRange(0, time_val * 10, padding=0)

# Axa Y:

half_screen_volts = volt_per_div * 4 self.plot.setYRange(−half_screen_volts, half_screen_volts, padding=0)

# Functionalitate on/off

def toggle_connection(self):
if self.btn_connect.isChecked():
port = self.port_input.text() self.serial_thread = SerialThread(port) self.serial_thread.samples_ready.connect(self. process_data)
self.serial_thread.start() self.btn_connect.setText("OFF")
else:
if self.serial_thread:
self.serial_thread.stop()
self.serial_thread = None
self.btn_connect.setText("ON")

def process_data(self, samples): self.total_samples_received += len(samples) now = time.time()
if now − self.last_time_check >= 1.0: self.measured_sps = self.total_samples_received / (now − self.last_time_check)

319 | self.total_samples_received = 0
320 | self.last_time_check = now
321 | # ăActualizm titlul ferestrei
322 | # self.plot.setTitle(f"NIBIRU SCOPE − Sampling:
| {self.measured_sps/1000:.1f} kSPS")
323
324 | # Buffer Management
325 | self.capture_buffer.extend(samples)
326 | if len(self.capture_buffer) > self.MAX_CAPTURE:
327 | self.capture_buffer = self.capture_buffer[−self.
| MAX_CAPTURE:]
328
329 | # Limitare FPS
330 | if now − self.last_draw_time < (1.0 / self.
| FPS_LIMIT):
331 | return
332
333
334 | time_per_div = TIME_STEPS[self.dial_time.value() ]
335 | total_time_screen = time_per_div * 10
336
337 | n_display_points = int(total_time_screen * self.
| measured_sps)
338
339 | n_display_points = max(10, min(n_display_points,
| len(self.capture_buffer)))
340
341 | if len(self.capture_buffer) < n_display_points
*
| 2:
342 | return
343
344 | # Procesare date
345 | # ăLum un chunk mare din ăcoad pentru a ăcuta
| trigger−ul
346 | # ăLum dublu cât ne trebuie ca ăs avem loc de
| ămanevr
347 | search_window = int(n_display_points * 2.5)
348 | if search_window > len(self.capture_buffer):
349 | search_window = len(self.capture_buffer)
350
351 | raw_data = np.array(self.capture_buffer[−
| search_window:], dtype=np.int16)
352
353 | # Filtru Median (doar ădac avem destule puncte)
354 | if len(raw_data) > 5:
355 | window = sliding_window_view(raw_data,
| window_shape=3)
356 | filtered_data = np.median(window, axis=1)
357 | else :
358 | filtered_data = raw_data
359
360 | # −−− 6. TRIGGER LOGIC −−−
361 | trig_adc = int((self.trigger_lvl / 5.0) * 1023)
362
363 | # Cautare rising edge
364 | binary = (filtered_data >= trig_adc).astype(np.
| int8)
365 | edges = np.diff(binary)
366 | trigger_indices = np.where(edges == 1)[0]

368 | frame_to_draw = None
369 | found_trigger = False
370
371 | if len(trigger_indices) > 0:
372
373 | for idx in reversed(trigger_indices):
374 | if idx + n_display_points < len(filtered_data):
375 | if np.all(filtered_data[idx+1 : idx+4] > (
| trig_adc − 20)):
376 | frame_to_draw = filtered_data[idx : idx +
| n_display_points]
377 | found_trigger = True
378
379 | self.lbl_trig_status.setText("LOCKED")
380 | self.lbl_trig_status.setStyleSheet("color: #00
| E676; border: 1px solid #00E676; font−weight:
| bold;")
381 | self.trigger_lost_timer = now
382 | break
383
384 | # Auto roll
385 | if not found_trigger:
386 | if now − self.trigger_lost_timer > 0.3:
387 | self.lbl_trig_status.setText("AUTO")
388 | self.lbl_trig_status.setStyleSheet("color:
| orange; border: 1px solid orange;")
389 | # Luam ultimele date disponibile
390 | if len(filtered_data) >= n_display_points:
391 | frame_to_draw = filtered_data[−n_display_points
| :]
392
393 | # Desenare
394 | if frame_to_draw is not None:
395 | self.last_draw_time = now
396
397 | # Conversie in Volti
398 | real_volts = (frame_to_draw / 1023.0) * 5.0
399
400 | display_volts = (real_volts − 2.5) + self.
| vert_offset
401
402 | # Generare axa timp
403 | total_time_screen = time_per_div * 10
404 | t = np.linspace(0, total_time_screen, len(
| display_volts))
405
406 | self.curve.setData(t, display_volts)
407
408 | if __name__ == "__main__":
409 | app = QApplication(sys.argv)
410 | window = MainWindow()
411 | window.show()
412 | sys.exit(app.exec_())

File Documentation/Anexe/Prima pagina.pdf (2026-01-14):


## Documentație APM

Prof. Coordonator: S. L. KERTESZ CSABA ZOLTAN Furtună Cristian
Iordache Denis-Ninel

BRAȘOV, 2026

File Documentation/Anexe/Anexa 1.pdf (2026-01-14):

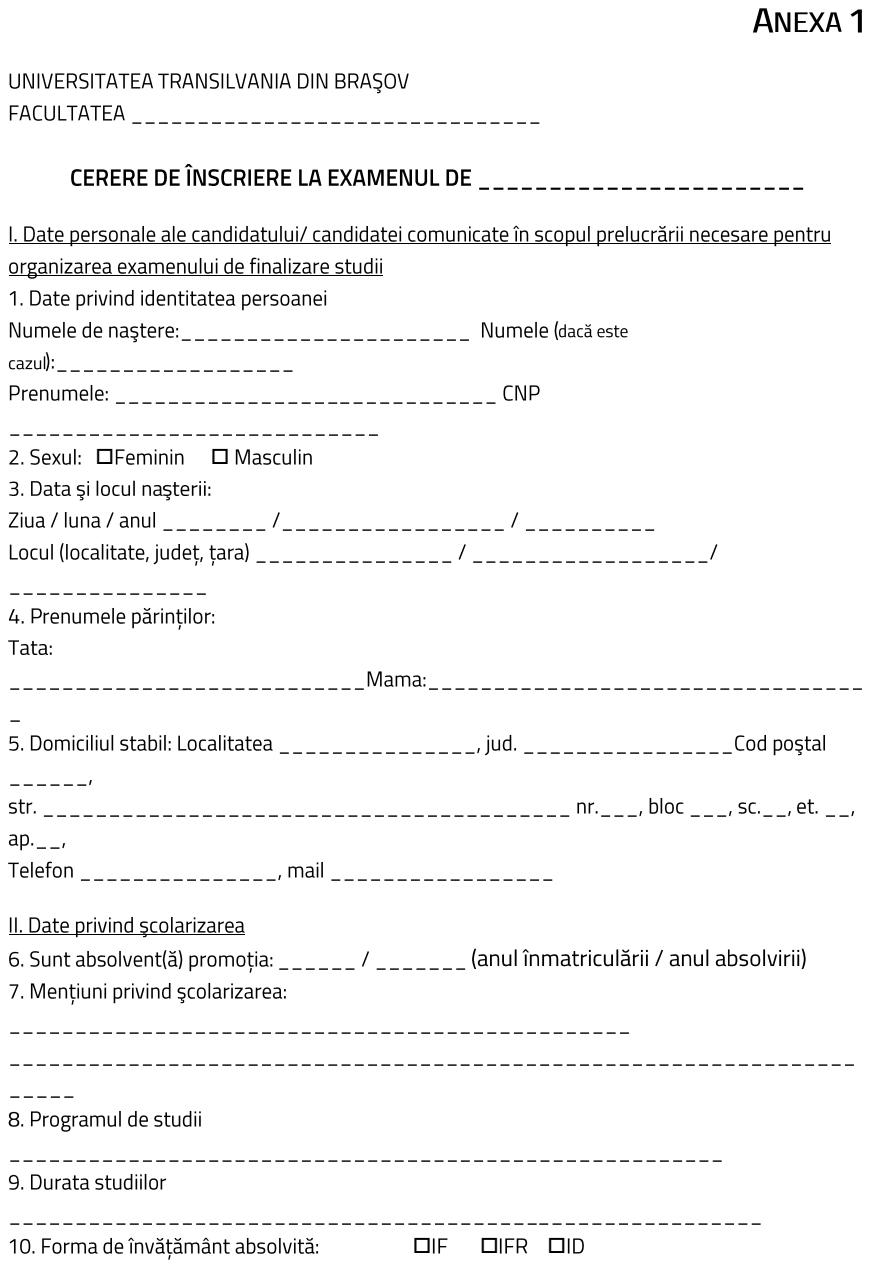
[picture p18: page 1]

☐ | ☐
☐ | ☐ | ☐

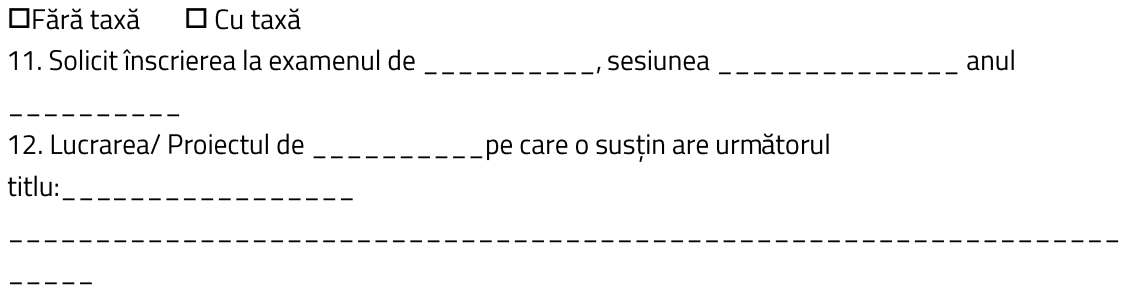
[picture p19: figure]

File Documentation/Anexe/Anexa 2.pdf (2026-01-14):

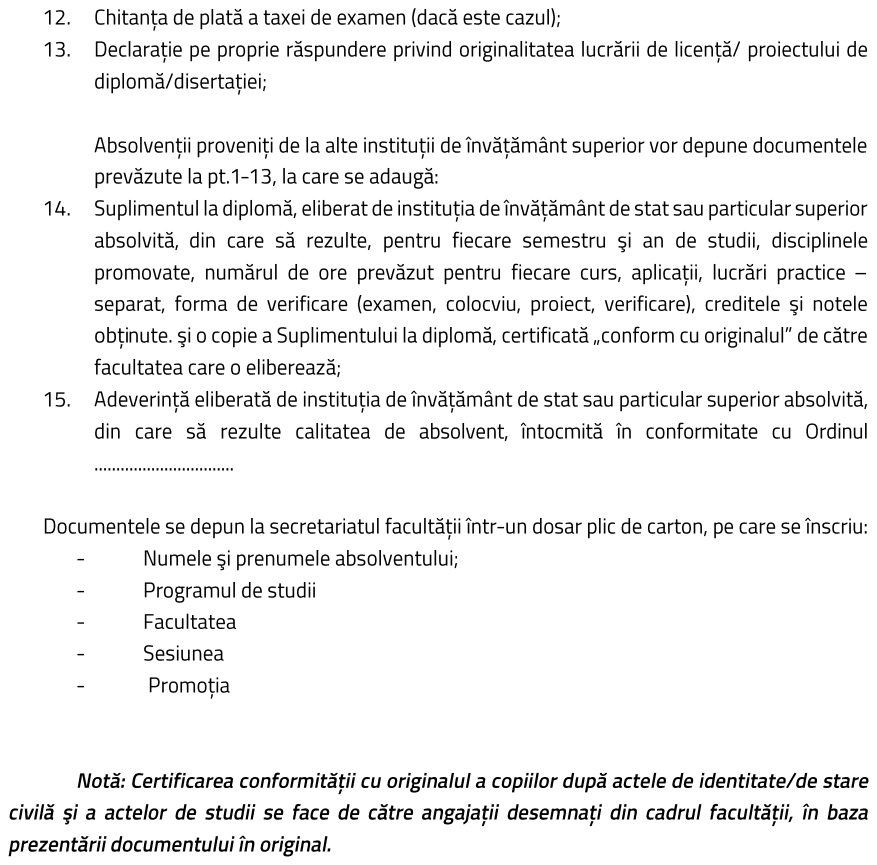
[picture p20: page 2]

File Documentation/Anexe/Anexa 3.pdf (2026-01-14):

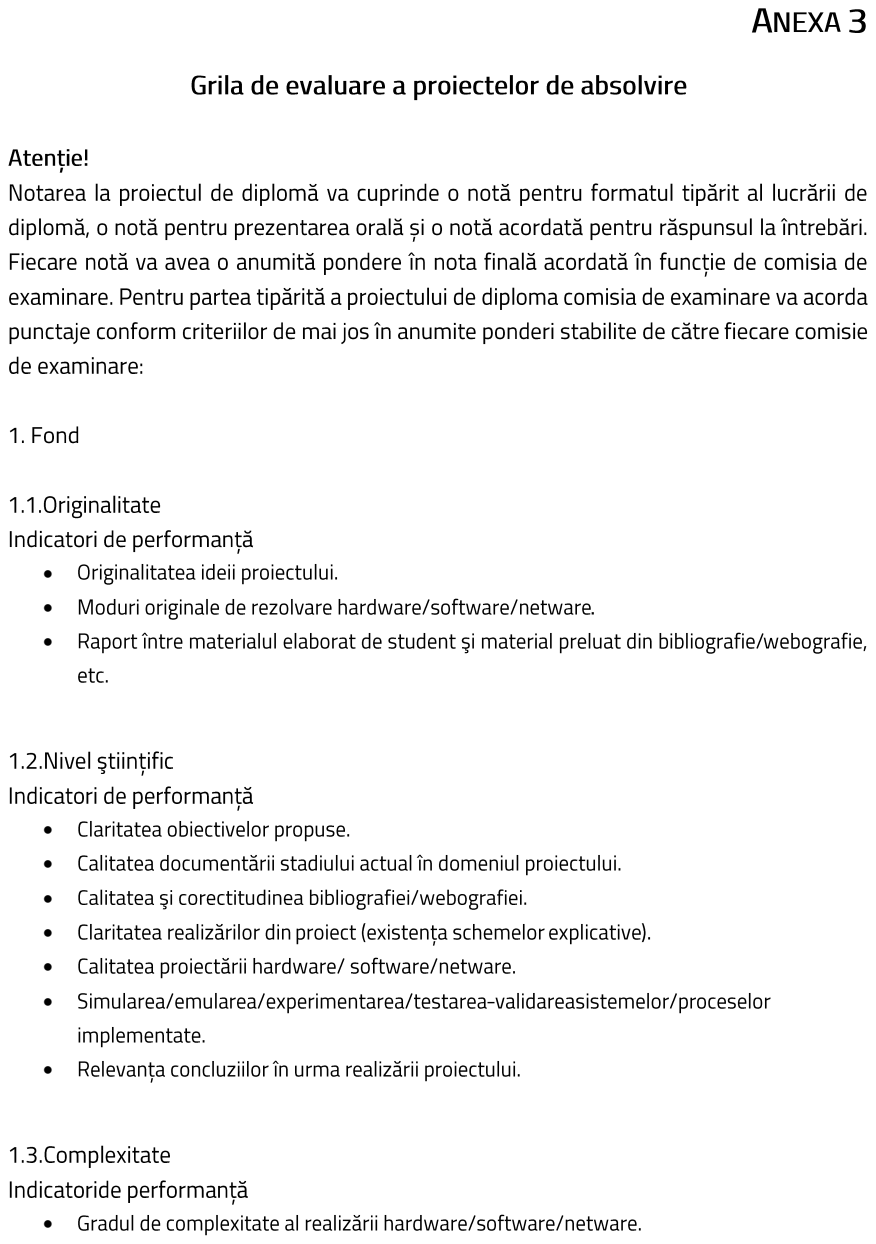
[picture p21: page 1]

•••••••••••

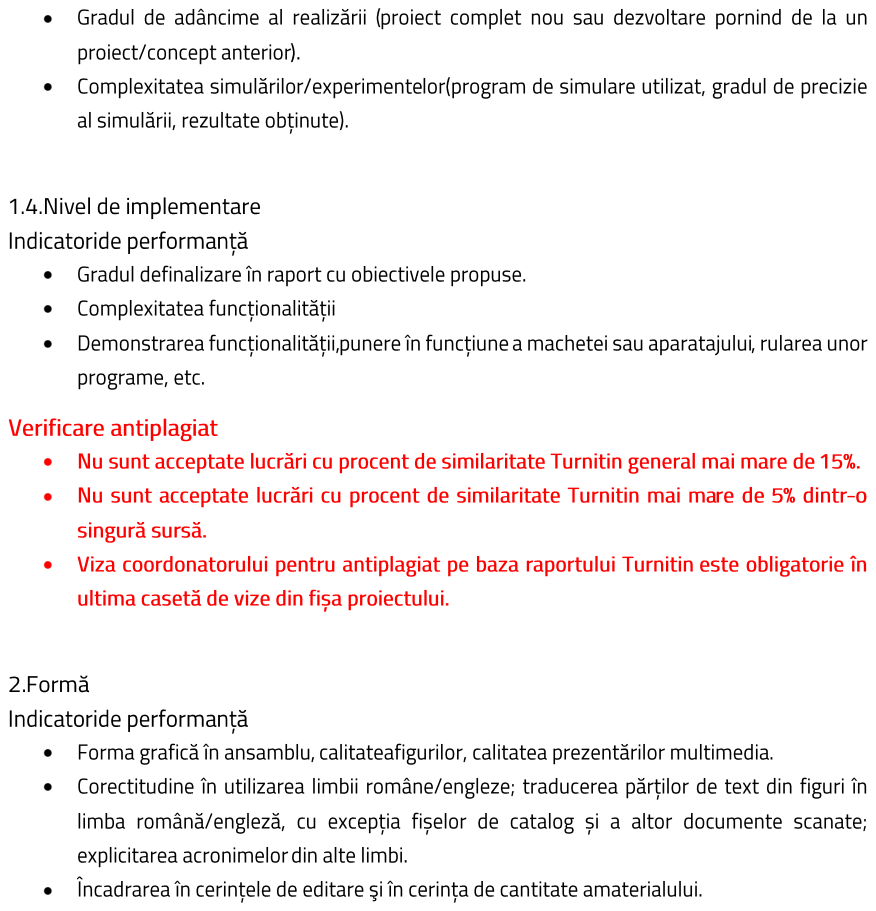
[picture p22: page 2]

•••••••••••

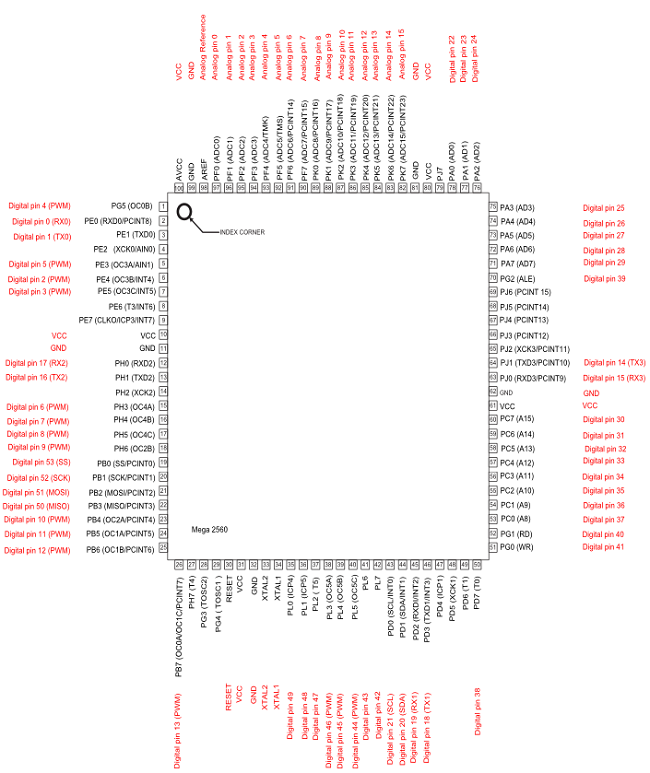
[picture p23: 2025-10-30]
Components/Datasheets and other resources/Arduino_mega_microcontroller_pinout.png

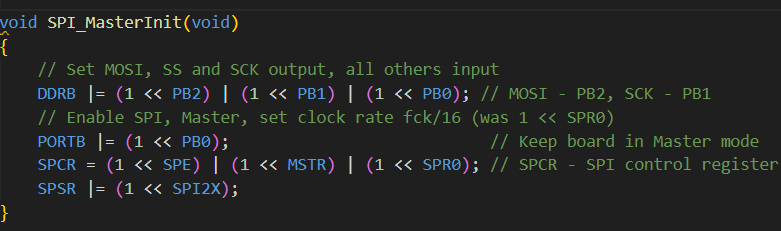
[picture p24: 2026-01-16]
Documentation/images/SPI_Master.png

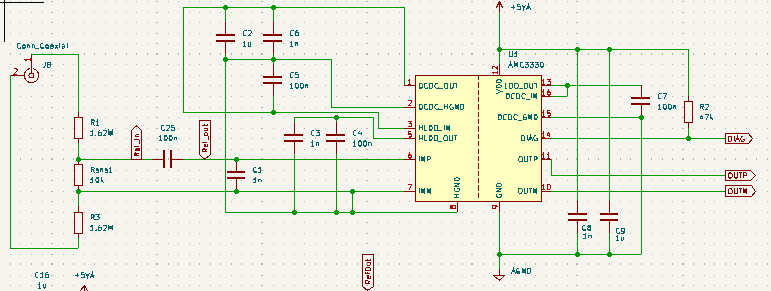
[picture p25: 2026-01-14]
Documentation/images/Intrare.png

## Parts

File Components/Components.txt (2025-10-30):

ATMEGA2560
ADUM3160

Module electronice:

--------conditionare semnal--------------
-Atenuator de intrare
-Amplificator de izolare
-Amplificator de instrumentatie/opamp

--------conversie semnal-----------------
-ADC (ADS 8681)

--------procesare semnal-----------------
-ATMEGA2560

--------transmisie date------------------
-uart / USB bridge?

--------alimentare-----------------------
-5V intern USB-c
-5V izolare USB-c
-eFuse TPS2595
-mufă pentru alimentare la baterie?

--------izolare usb----------------------
-ADUM3160

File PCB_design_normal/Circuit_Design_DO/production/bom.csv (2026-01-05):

Designator | Footprint | Quantity | Value | LCSC Part #
C1 | 0805 | 1 | 1n | C1710
C10, C11 | 0805 | 2 | 0.1u | C1711
C12 | 0805 | 1 | 3.3n | C1738
C13, C3, C6, C8 | 0805 | 4 | 1n | C1791
C14, C15, C16, C17, C2, C9 | 0805 | 6 | 1u | C1712
C18 | 0805 | 1 | 22u | C5674
C19, C20 | 0805 | 2 | 10p | C107107
C21, C22, C23, C25, C28, C29, C30, C31, C32, C33, C34, C37, C4, C5, C7 | 0805 | 15 | 100n | C1711
C24, C35 | 0805 | 2 | 10n | C1804
C26, C27 | 0805 | 2 | 47pF | C14857
C36 | CP_EIA-6032-28_Kemet-C | 1 | 10uF | C7209
D1 | D_SMF | 1 | SMF5V0A | C1972946
D2 | 0805 | 1 | LED_PWR_R | C86865
D3 | 0805 | 1 | LED_BUILTIN | C2904378
D4 | D_SOD-123 | 1 | 1N4148W | C2099
D5 | 0805 | 1 | TX_LED_Y | C2904378
D6 | 0805 | 1 | RX_LED_Y | C2904378
D7 | 0805 | 1 | SUS_LED_Y | C2904378
F1 | 0805 | 1 | 500mA | C20977
J1 | PinHeader_1x06_P2.54mm_Vertical | 1 | Power
J10 | PinHeader_2x03_P2.54mm_Vertical | 1 | ICSP
J2 | PinHeader_1x08_P2.54mm_Vertical | 1 | ~
J3, J5 | PinHeader_1x08_P2.54mm_Vertical | 2 | Analog
J4 | PinHeader_1x08_P2.54mm_Vertical | 1 | PWM
J6 | PinHeader_1x08_P2.54mm_Vertical | 1 | COMUNICATION
J7 | PinHeader_2x18_P2.54mm_Vertical | 1 | Digital
J8 | BNC_Amphenol_B6252HB-NPP3G-50_Horizontal | 1 | Conn_Coaxial | C2837587
J9 | USB_C_Receptacle_GCT_USB4105-xx-A_16P_TopMnt_Horizontal | 1 | USB_C_Receptacle_USB2.0_16P | C393939
K3 | Relay_DPDT_Omron_G6K-2F-Y | 1 | G6K-2 | C2982926
Q2 | SOT-23 | 1 | SS8050 | C2150
R1, R3 | 0805 | 2 | 1.62M | C189667
R10, R11 | 0805 | 2 | 5.1k | C702837
R12, R13, R27 | 0805 | 3 | 27R | C17594
R14, R16, R18, R19, R29, R8, R9 | 0805 | 7 | 1k | C702831
R15, R20 | 0805 | 2 | 9k | C247026
R17, R21 | 0805 | 2 | 0.1R | C125639
R2 | 0805 | 1 | 47k | C702826
R22, R25, R28, R36, R37, R38, R39, R40, R41, R43, R5, RSNS1 | 0805 | 12 | 10k | C702829
R23, R24 | 0805 | 2 | 49.9 | C17720
R26 | 0805 | 1 | 1M | C17514
R30, R31, R35, R42 | 0805 | 4 | 2.4k | C22370006
R32, R33, R34 | 0805 | 3 | 300R | C22356757
R4 | 0805 | 1 | 1780 | C17397
R6 | 0805 | 1 | 332k | C17631
R7 | 0805 | 1 | 118k | C17427
SW1 | Switch_Tactile_SMD_6x6mm | 1 | Reset | C2845322
SW2, SW3 | RotaryEncoder_Alps_EC11E_Vertical_H20mm | 2 | RotaryEncoder | C370986
SW4 | Switch_Tactile_SMD_6x6mm | 1 | AC/DC | C2845322
U1 | SOIC-16W_7.5x10.3mm_P1.27mm | 1 | AMC3330 | C5214212
U10 | QFN-16-1EP_4x4mm_P0.65mm_EP2.1x2.1mm | 1 | FT230XQ | C128629
U11, U6, U9 | SMD-4_4.4x3.85mm_P2.54mm | 3 | LTV-356T | C10804
U12 | SOIC-16W_7.5x10.3mm_P1.27mm | 1 | ADuM1401xRW | C33273
U13 | VSSOP-10_3x3mm_P0.5mm | 1 | TS5A23159DGS | C42751
U2 | Converter_DCDC_TRACO_TEA1-xxxx_THT | 1 | TEA1-0505 | C5291394
U3 | DSG0008A | 1 | TPS259571DSGR | C471038
U4 | RGE24_2P7X2P7_TEX | 1 | ADS8920BRGET | C1542899
U5 | VSSOP-8_3x3mm_P0.65mm | 1 | THS4521IDGK | C170157
U7 | SOIC-8_3.9x4.9mm_P1.27mm | 1 | REF5045AD | C1575525
U8 | TQFP-100_14x14mm | 1 | ATMEGA2560-16AU | C22460
Y1 | Crystal_SMD_5032-2Pin_5.0x3.2mm | 1 | 16MHz | C242221

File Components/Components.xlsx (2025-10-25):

Componenta | Pret | Link | Obs
BNC | $1.31 | https://jlcpcb.com/partdetail/cntitle-BNCKY/C20415778 | BNC
BAV199 | $0.02 - $0.03 | https://jlcpcb.com/partdetail/70084-BAV199/C68971 | switching diodes
B59850C0130A070 | $0.60 | https://jlcpcb.com/partdetail/TDK-B59850C0130A070/C125471 | termistor
TLV9062IDR | $0.08 | https://jlcpcb.com/partdetail/TexasInstruments-TLV9062IDR/C398355 | op amp buffer pt ADC (doar unul)
OPA365AIDBVR | $0.46 | https://jlcpcb.com/partdetail/TexasInstruments-OPA365AIDBVR/C96626
OPA320AIDBVR | $0.61 | https://jlcpcb.com/partdetail/TexasInstruments-OPA320AIDBVR/C92494
G6K2GYDC3 | $1.34 | https://jlcpcb.com/partdetail/OmronElectronics-G6K2GYDC3/C1525299 | signal relays
AD7988-5BRMZ-RL7 | $11.75 | https://jlcpcb.com/partdetail/AnalogDevices-AD7988_5BRMZRL7/C578585 | ADC 16-bit, 500ksps
LTC1864CMS8#PBF | $14.22 | https://jlcpcb.com/partdetail/AnalogDevices-LTC1864CMS8PBF/C107763 | ADC 16-bit, 250ksps
ADS7883SDBVT | $10.99 | https://jlcpcb.com/partdetail/TexasInstruments-ADS7883SDBVT/C122523 | ADC 12-bit, 3Msps
ADS7886SDBVT | $6.24 | https://jlcpcb.com/partdetail/TexasInstruments-ADS7886SDBVT/C2669795 | ADC 12-bit, 1Msps
ADR4525ARZ-R7 | $4.95 | https://jlcpcb.com/partdetail/AnalogDevices-ADR4525ARZR7/C403698 | Vref ADC 2.5V
REF5050AIDR | $0.70 | https://jlcpcb.com/partdetail/TexasInstruments-REF5050AIDR/C27804 | Vref ADC 5V
SN74AXC4T245RSVR | $0.60 | https://jlcpcb.com/partdetail/TexasInstruments-SN74AXC4T245RSVR/C2677409 | SPI level translator
EC11E1834403 | $1.90 | https://jlcpcb.com/partdetail/ALPSALPINE-EC11E1834403/C361165 | Rotary Encoder
TLV3501AIDBVRG4 | $1.13 | https://jlcpcb.com/partdetail/TexasInstruments-TLV3501AIDBVRG4/C3658928 | Trigger comparator
MCP4921-E/SN | $2.21 | https://jlcpcb.com/partdetail/MicrochipTech-MCP4921_ESN/C43499 | Trigger threshold src
CP2102N-A02-GQFN28R | $1.52 | https://jlcpcb.com/partdetail/1049893-CP2102N_A02GQFN28R/C964632 | USB-UART bridge

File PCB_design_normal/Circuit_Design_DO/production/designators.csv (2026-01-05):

5VA:1
AGND:1
C1:1
C10:1
C11:1
C12:1
C13:1
C14:1
C15:1
C16:1
C17:1
C18:1
C19:1
C2:1
C20:1
C21:1
C22:1
C23:1
C24:1
C25:1
C26:1
C27:1
C28:1
C29:1
C3:1
C30:1
C31:1
C32:1
C33:1
C34:1
C35:1
C36:1
C37:1
C4:1
C5:1
C6:1
C7:1
C8:1
C9:1
D1:1
D2:1
D3:1
D4:1
D5:1
D6:1
D7:1
F1:1
H1:1
H2:1
H3:1
H4:1
J1:1
J10:1
J2:1
J3:1
J4:1
J5:1
J6:1
J7:1
J8:1
J9:1
K3:1
Q2:1
R1:1
R10:1
R11:1
R12:1
R13:1
R14:1
R15:1
R16:1
R17:1
R18:1
R19:1
R2:1
R20:1
R21:1
R22:1
R23:1
R24:1
R25:1
R26:1
R27:1
R28:1
R29:1
R3:1
R30:1
R31:1
R32:1
R33:1
R34:1
R35:1
R36:1
R37:1
R38:1
R39:1
R4:1
R40:1
R41:1
R42:1
R43:1
R5:1
R6:1
R7:1
R8:1
R9:1
RSNS1:1
SW1:1
SW2:1
SW3:1
SW4:1
U1:1
U10:1
U11:1
U12:1
U13:1
U2:1
U3:1
U4:1
U5:1
U6:1
U7:1
U8:1
U9:1
Y1:1

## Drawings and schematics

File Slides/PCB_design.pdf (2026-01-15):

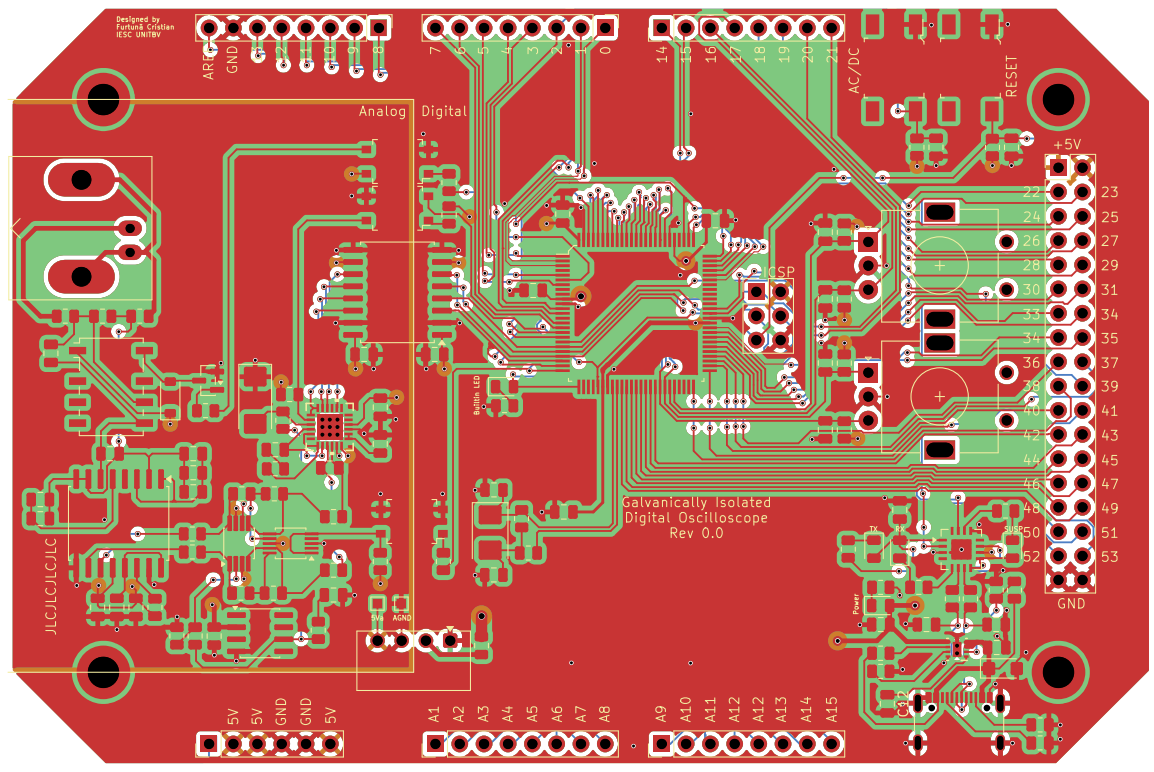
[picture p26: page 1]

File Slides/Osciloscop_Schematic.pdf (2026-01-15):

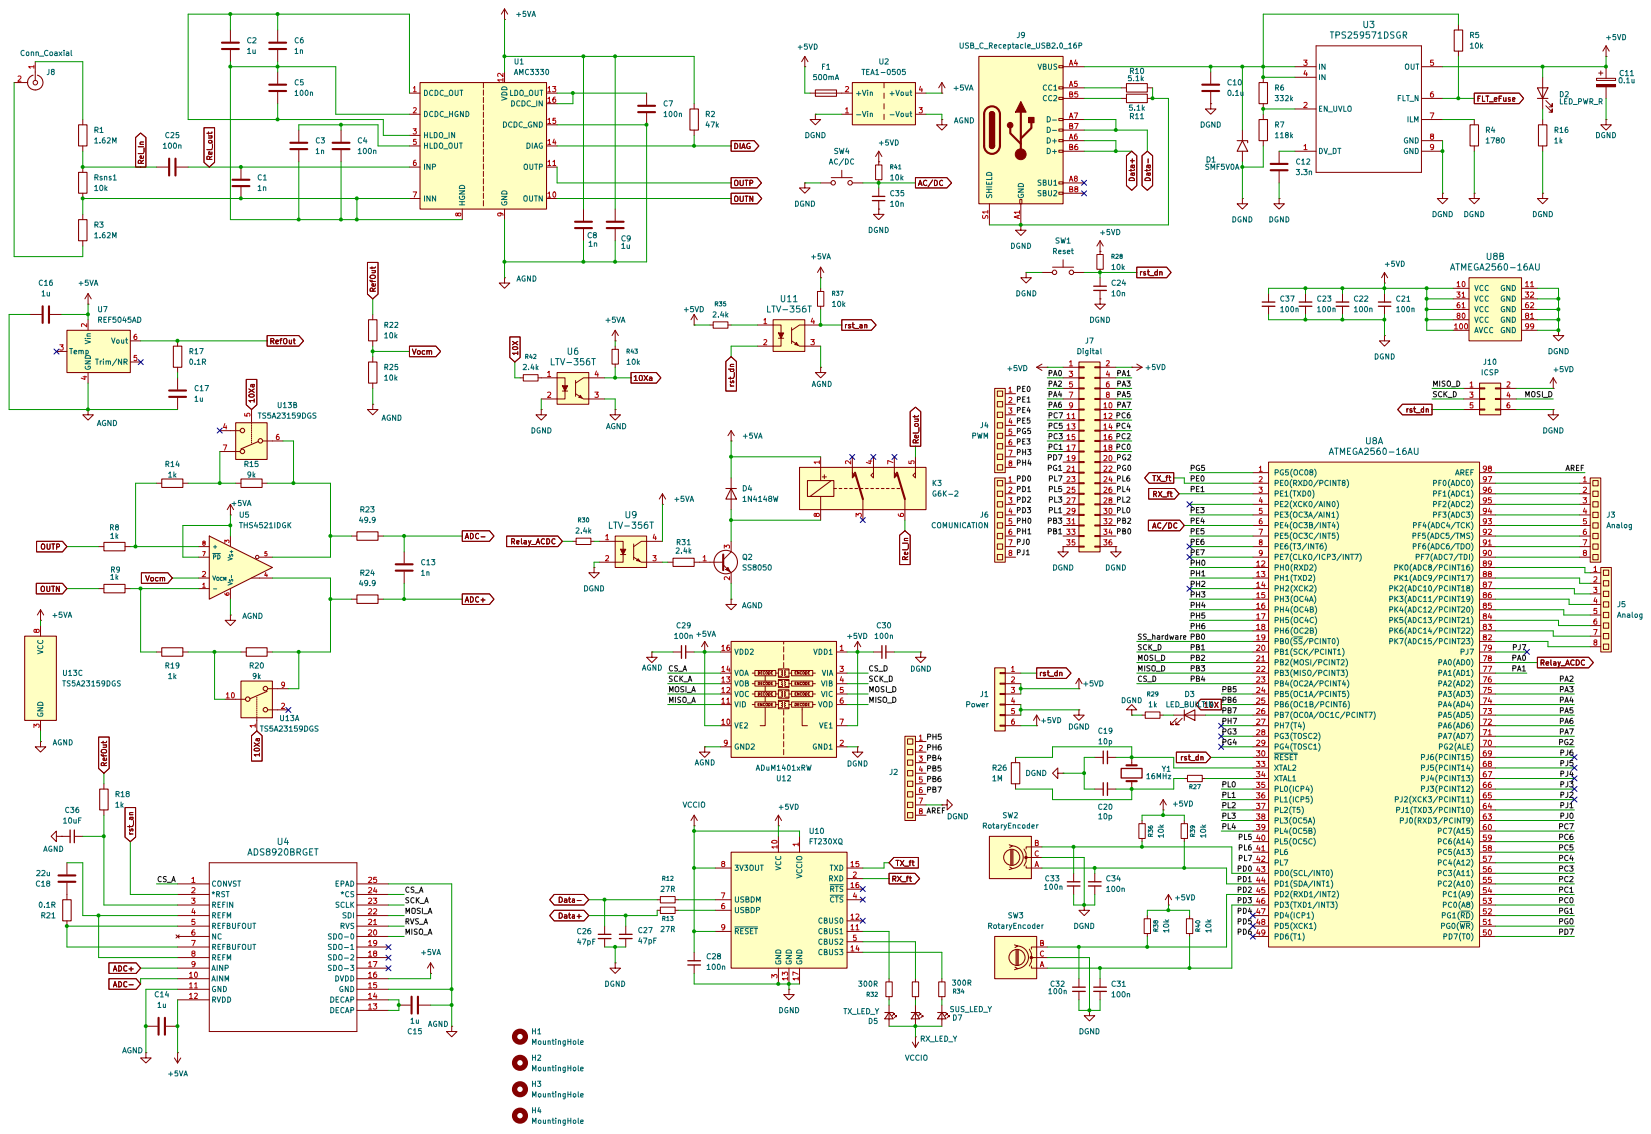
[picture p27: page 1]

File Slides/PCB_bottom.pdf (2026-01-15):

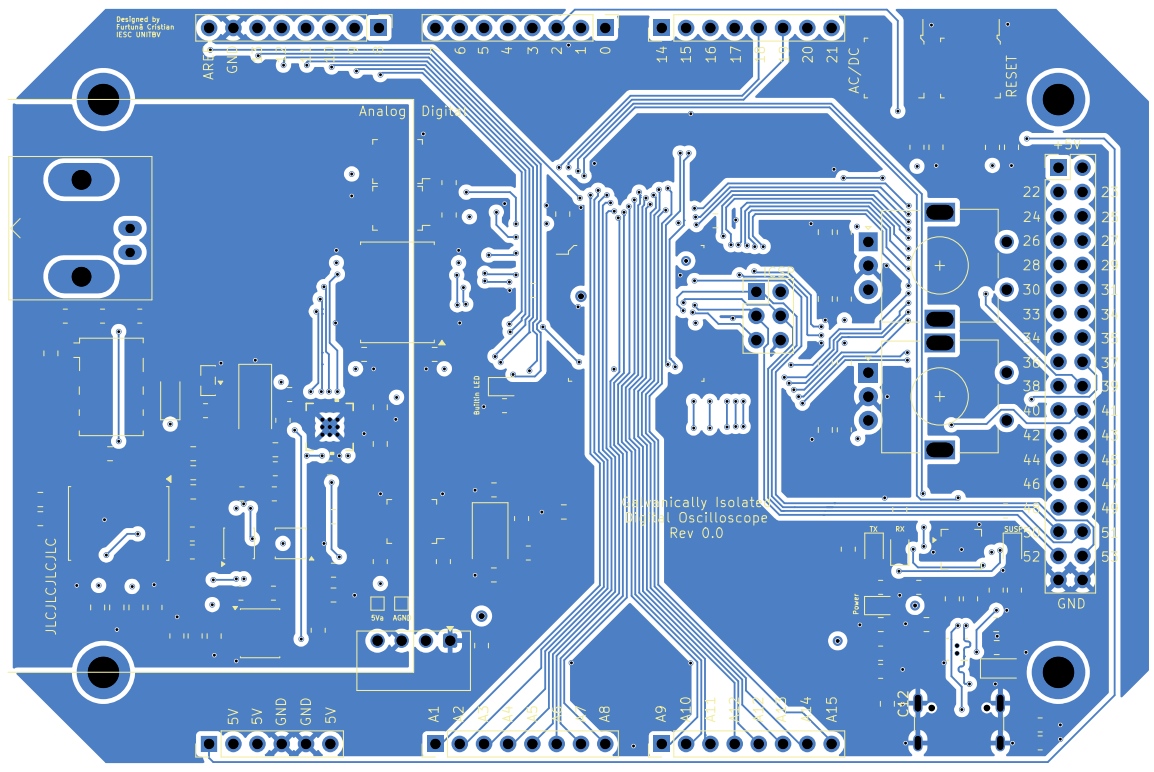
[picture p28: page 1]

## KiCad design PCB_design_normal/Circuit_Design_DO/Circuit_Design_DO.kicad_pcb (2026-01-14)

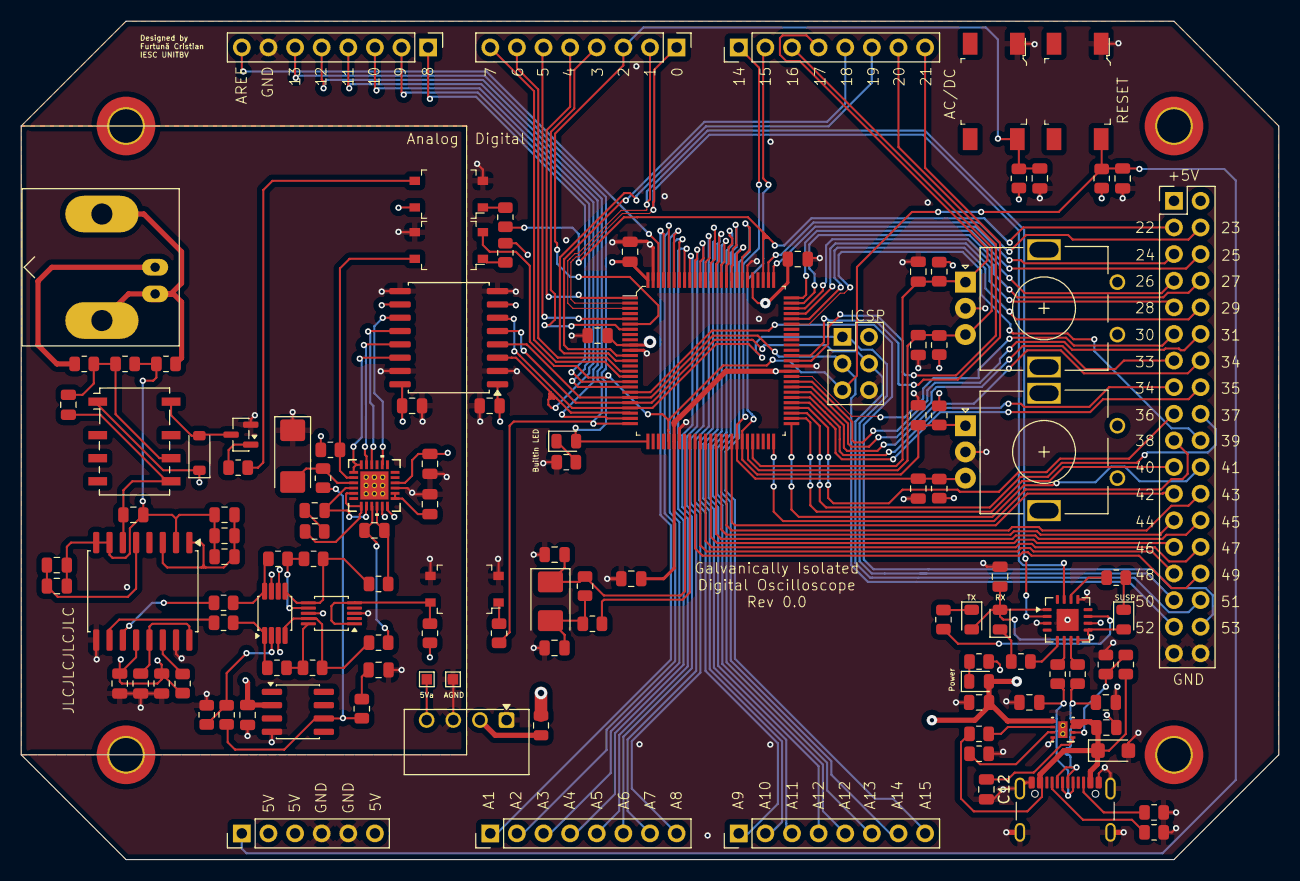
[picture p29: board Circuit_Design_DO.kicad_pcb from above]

Board: 4 copper layers, 120.0 x 80.0 mm, 125 parts (0 on the bottom side), 139 nets.

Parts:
5Va: TestPoint_Pad_1.0x1.0mm
AGND: TestPoint_Pad_1.0x1.0mm
C1, C3, C6, C8, C13: 1n; C_0805_2012Metric
C2, C9, C14, C15, C16, C17: 1u; C_0805_2012Metric
C4, C5, C7, C21, C22, C23, C25, C28, C29, C30, C31, C32, C33, C34, C37: 100n; C_0805_2012Metric
C10, C11: 0.1u; C_0805_2012Metric
C12: 3.3n; C_0805_2012Metric
C18: 22u; C_0805_2012Metric
C19, C20: 10p; C_0805_2012Metric
C24, C35: 10n; C_0805_2012Metric
C26, C27: 47pF; C_0805_2012Metric
C36: 10uF; CP_EIA-6032-28_Kemet-C
D1: SMF5V0A; D_SMF
D2: LED_PWR_R; LED_0805_2012Metric
D3: LED_BUILTIN; LED_0805_2012Metric
D4: 1N4148W; D_SOD-123
D5: TX_LED_Y; LED_0805_2012Metric
D6: RX_LED_Y; LED_0805_2012Metric
D7: SUS_LED_Y; LED_0805_2012Metric
F1: 500mA; Fuse_0805_2012Metric
H1, H2, H3, H4: MountingHole; MountingHole_3.2mm_M3_DIN965_Pad_TopBottom
J1: Power; PinHeader_1x06_P2.54mm_Vertical
J2: PinHeader_1x08_P2.54mm_Vertical
J3, J5: Analog; PinHeader_1x08_P2.54mm_Vertical
J4: PWM; PinHeader_1x08_P2.54mm_Vertical
J6: COMUNICATION; PinHeader_1x08_P2.54mm_Vertical
J7: Digital; PinHeader_2x18_P2.54mm_Vertical
J8: Conn_Coaxial; BNC_Amphenol_B6252HB-NPP3G-50_Horizontal
J9: USB_C_Receptacle_USB2.0_16P; USB_C_Receptacle_GCT_USB4105-xx-A_16P_TopMnt_Horizontal
J10: ICSP; PinHeader_2x03_P2.54mm_Vertical
K3: G6K-2; Relay_DPDT_Omron_G6K-2F-Y
Q2: SS8050; SOT-23
R1, R3: 1.62M; R_0805_2012Metric
R2: 47k; R_0805_2012Metric
R4: 1780; R_0805_2012Metric
R5, R22, R25, R28, R36, R37, R38, R39, R40, R41, R43: 10k; R_0805_2012Metric
R6: 332k; R_0805_2012Metric
R7: 118k; R_0805_2012Metric
R8, R9, R14, R16, R18, R19, R29: 1k; R_0805_2012Metric
R10, R11: 5.1k; R_0805_2012Metric
R12, R13, R27: 27R; R_0805_2012Metric
R15, R20: 9k; R_0805_2012Metric
R17, R21: 0.1R; R_0805_2012Metric
R23, R24: 49.9; R_0805_2012Metric
R26: 1M; R_0805_2012Metric
R30, R31, R35, R42: 2.4k; R_0805_2012Metric
R32, R33, R34: 300R; R_0805_2012Metric
Rsns1: 10k; R_0805_2012Metric
SW1: Reset; Switch_Tactile_SMD_6x6mm
SW2, SW3: RotaryEncoder; RotaryEncoder_Alps_EC11E_Vertical_H20mm
SW4: AC/DC; Switch_Tactile_SMD_6x6mm
U1: AMC3330; SOIC-16W_7.5x10.3mm_P1.27mm
U2: TEA1-0505; Converter_DCDC_TRACO_TEA1-xxxx_THT
U3: TPS259571DSGR; DSG0008A
U4: ADS8920BRGET; RGE24_2P7X2P7_TEX
U5: THS4521IDGK; VSSOP-8_3x3mm_P0.65mm
U6, U9, U11: LTV-356T; SMD-4_4.4x3.85mm_P2.54mm
U7: REF5045AD; SOIC-8_3.9x4.9mm_P1.27mm
U8: ATMEGA2560-16AU; TQFP-100_14x14mm
U10: FT230XQ; QFN-16-1EP_4x4mm_P0.65mm_EP2.1x2.1mm
U12: ADuM1401xRW; SOIC-16W_7.5x10.3mm_P1.27mm
U13: TS5A23159DGS; VSSOP-10_3x3mm_P0.5mm
Y1: 16MHz; Crystal_SMD_5032-2Pin_5.0x3.2mm

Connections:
10X: J2.5, R42.1, U8.25 (PB6(OC1B/PCINT6))
10Xa: R43.2, U6.4, U13.1, U13.5
+5VA: 5Va.1, C8.1, C9.1, C14.2, C16.1, C29.2, D4.1 (K), K3.1, R2.1, R37.1, R43.1, U1.12 (VDD), U2.4 (+Vout), U4.12 (RVDD), U4.16 (DVDD), U5.3 (V_{S+}), U5.7 (~PD), U7.2 (Vin), U9.4, U12.10 (VE2), U12.16 (VDD2), U13.8 (VCC)
+5VD: C11.1, C21.1, C22.1, C23.1, C30.1, C37.1, D2.2 (A), F1.1, J1.2, J1.3, J1.6, J7.1, J7.2, J10.2, R28.2, R35.1, R36.2, R38.2, R39.2, R40.2, R41.2, U3.5 (OUT), U8.10 (VCC), U8.31 (VCC), U8.61 (VCC), U8.80 (VCC), U8.100 (AVCC), U10.10 (VCC), U12.1 (VDD1), U12.7 (VE1)
/AREF: J2.8, U8.98 (AREF)
/CS_A: U4.1 (CONVST), U4.24 (*CS), U12.14 (VOA)
/CS_D: J2.3, U8.23 (PB4(OC2A/PCINT4)), U12.3 (VIA)
/MISO_A: U4.20 (SDO-0), U12.11 (VID)
/MISO_D: J7.31, J10.1, U8.22 (PB3(MISO/PCINT3)), U12.6 (VOD)
/MOSI_A: U4.22 (SDI), U12.12 (VOC)
/MOSI_D: J7.32, J10.4, U8.21 (PB2(MOSI/PCINT2)), U12.5 (VIC)
/PA1: J7.4, U8.77 (PA1(AD1))
/PA2: J7.5, U8.76 (PA2(AD2))
/PA3: J7.6, U8.75 (PA3(AD3))
/PA4: J7.7, U8.74 (PA4(AD4))
/PA5: J7.8, U8.73 (PA5(AD5))
/PA6: J7.9, U8.72 (PA6(AD6))
/PA7: J7.10, U8.71 (PA7(AD7))
/PB0: J7.34, U8.19 (PB0(~SS/PCINT0))
/PB1: J7.33, J10.3, U8.20 (PB1(SCK/PCINT1)), U12.4 (VIB)
/PB5: J2.4, U8.24 (PB5(OC1A/PCINT5))
/PB7: D3.2 (A), J2.6, U8.26 (PB7(OC0A/OC1C/PCINT7))
/PC0: J7.18, U8.53 (PC0(A8))
/PC1: J7.17, U8.54 (PC1(A9))
/PC2: J7.16, U8.55 (PC2(A10))
/PC3: J7.15, U8.56 (PC3(A11))
/PC4: J7.14, U8.57 (PC4(A12))
/PC5: J7.13, U8.58 (PC5(A13))
/PC6: J7.12, U8.59 (PC6(A14))
/PC7: J7.11, U8.60 (PC7(A15))
/PD0: C33.1, J6.1, R36.1, SW2.B, U8.43 (PD0(SCL/INT0))
/PD1: C34.1, J6.2, R39.1, SW2.A, U8.44 (PD1(SDA/INT1))
/PD2: C32.1, J6.3, R38.1, SW3.B, U8.45 (PD2(RXD1/INT2))
/PD3: C31.1, J6.4, R40.1, SW3.A, U8.46 (PD3(TXD1/INT3))
/PD7: J7.19, U8.50 (PD7(T0))
/PE3: J4.6, U8.5 (PE3(OC3A/AIN1))
/PE5: J4.4, U8.7 (PE5(OC3C/INT5))
/PG0: J7.22, U8.51 (PG0(~WR))
/PG1: J7.21, U8.52 (PG1(~RD))
/PG2: J7.20, U8.70 (PG2(ALE))
/PG5: J4.5, U8.1 (PG5(OC08))
/PH0: J6.5, U8.12 (PH0(RXD2))
/PH1: J6.6, U8.13 (PH1(TXD2))
/PH3: J4.7, U8.15 (PH3(OC4A))
/PH4: J4.8, U8.16 (PH4(OC4B))
/PH5: J2.1, U8.17 (PH5(OC4C))
/PH6: J2.2, U8.18 (PH6(OC2B))
/PJ0: J6.7, U8.63 (PJ0(RXD3/PCINT9))
/PJ1: J6.8, U8.64 (PJ1(TXD3/PCINT10))
/PL0: J7.30, U8.35 (PL0(ICP4))
/PL1: J7.29, U8.36 (PL1(ICP5))
/PL2: J7.28, U8.37 (PL2(T5))
/PL3: J7.27, U8.38 (PL3(OC5A))
/PL4: J7.26, U8.39 (PL4(OC5B))
/PL5: J7.25, U8.40 (PL5(OC5C))
/PL6: J7.24, U8.41 (PL6)
/PL7: J7.23, U8.42 (PL7)
/SCK_A: U4.23 (SCLK), U12.13 (VOB)
AC/DC: C35.1, J4.3, R41.1, SW4.2, U8.6 (PE4(OC3B/INT4))
ADC+: C13.2, R24.2, U4.9 (AINP)
ADC-: C13.1, R23.1, U4.10 (AINM)
AGND: AGND.1, C7.2, C8.2, C9.2, C14.1, C15.2, C16.2, C17.2, C29.1, C36.1, Q2.2 (E), R25.2, U1.9 (GND), U1.15 (DCDC_GND), U2.3 (-Vout), U4.11 (GND), U4.15 (GND), U4.25 (EPAD), U4.V, U5.6 (V_{S-}), U6.3, U7.4 (GND), U11.3, U12.9 (GND2), U12.15 (GND2), U13.3 (GND)
DGND: C10.2, C11.2, C12.2, C19.1, C20.2, C21.2, C22.2, C23.2, C24.2, C26.1, C27.1, C28.1, C30.2, C31.2, C32.2, C33.2, C34.2, C35.2, C37.2, D1.2 (A2), J1.4, J1.5, J2.7, J7.35, J7.36, J9.A1 (GND), J9.A12 (GND), J9.B1 (GND), J9.B12 (GND), J9.S1 (SHIELD), J10.6, R4.2, R7.2, R10.2, R11.2, R16.2, R29.1, SW1.1, SW2.C, SW3.C, SW4.1, U2.1 (-Vin), U3.8 (GND), U3.9 (GND), U3.V, U6.2, U8.11 (GND), U8.32 (GND), U8.62 (GND), U8.81 (GND), U8.99 (GND), U9.2, U10.3 (GND), U10.13 (GND), U10.17 (GND), U12.2 (GND1), U12.8 (GND1)
DIAG: R2.2, U1.14 (DIAG)
Data+: C27.2, J9.A6 (D+), J9.B6 (D+), R13.1
Data-: C26.2, J9.A7 (D-), J9.B7 (D-), R12.1
FLT_eFuse: R5.2, U3.6 (FLT_N)
unnamed: C15.1, U4.13 (DECAP), U4.14 (DECAP)
unnamed: C17.1, R17.2
unnamed: C18.1, R21.2
unnamed: C18.2, U4.4 (REFM), U4.8 (REFM)
unnamed: C20.1, R26.2, R27.1, Y1.2
unnamed: C10.1, D1.1 (A1), J9.A4 (VBUS), J9.A9 (VBUS), J9.B4 (VBUS), J9.B9 (VBUS), R5.1, R6.1, U3.3 (IN), U3.4 (IN)
unnamed: D2.1 (K), R16.1
unnamed: D3.1 (K), R29.2
unnamed: D4.2 (A), K3.8, Q2.3 (C)
unnamed: D5.1 (K), R32.1
unnamed: D6.1 (K), R33.1
unnamed: D7.1 (K), R34.1
unnamed: J8.2 (Ext), R3.2
unnamed: J8.1 (In), R1.1
unnamed: J9.A5 (CC1), R10.1
unnamed: J9.B5 (CC2), R11.1
unnamed: Q2.1 (B), R31.2
unnamed: R14.1, R15.1, U13.7
unnamed: R15.2, R23.2, U5.5, U13.6
unnamed: R19.1, R20.1, U13.10
unnamed: R20.2, R24.1, U5.4, U13.9
unnamed: R21.1, U4.5 (REFBUFOUT), U4.7 (REFBUFOUT)
unnamed: R30.2, U9.1
unnamed: R31.1, U9.3
unnamed: R35.2, U11.1
unnamed: R42.2, U6.1
unnamed: C1.2, C2.2, C3.2, C4.2, C5.1, C6.2, R3.1, Rsns1.2, U1.2 (DCDC_HGND), U1.7 (INN), U1.8 (HGND)
unnamed: C7.1, U1.13 (LDO_OUT), U1.16 (DCDC_IN)
unnamed: C2.1, C5.2, C6.1, U1.1 (DCDC_OUT), U1.3 (HLDO_IN)
unnamed: C3.1, C4.1, U1.5 (HLDO_OUT)
unnamed: F1.2, U2.2 (+Vin)
unnamed: C12.1, U3.1 (DV_DT)
unnamed: R6.2, R7.1, U3.2 (EN_UVLO)
unnamed: R4.1, U3.7 (ILM)
unnamed: C36.2, R18.1, U4.3 (REFIN)
unnamed: R8.2, R14.2, U5.8 (+)
unnamed: R9.2, R19.2, U5.1 (-)
unnamed: J3.1, U8.97 (PF0(ADC0))
unnamed: J3.2, U8.96 (PF1(ADC1))
unnamed: J3.3, U8.95 (PF2(ADC2))
unnamed: J3.4, U8.94 (PF3(ADC3))
unnamed: J3.5, U8.93 (PF4(ADC4/TCK))
unnamed: J3.6, U8.92 (PF5(ADC5/TMS))
unnamed: J3.7, U8.91 (PF6(ADC6/TDO))
unnamed: J3.8, U8.90 (PF7(ADC7/TDI))
unnamed: J5.1, U8.89 (PK0(ADC8/PCINT16))
unnamed: J5.2, U8.88 (PK1(ADC9/PCINT17))
unnamed: J5.3, U8.87 (PK2(ADC10/PCINT18))
unnamed: J5.4, U8.86 (PK3(ADC11/PCINT19))
unnamed: J5.5, U8.85 (PK4(ADC12/PCINT20))
unnamed: J5.6, U8.84 (PK5(ADC13/PCINT21))
unnamed: J5.7, U8.83 (PK6(ADC14/PCINT22))
unnamed: J5.8, U8.82 (PK7(ADC15/PCINT23))
unnamed: R27.2, U8.34 (XTAL1)
unnamed: C19.2, R26.1, U8.33 (XTAL2), Y1.1
unnamed: R32.2, U10.11 (CBUS1)
unnamed: R33.2, U10.5 (CBUS2)
unnamed: R34.2, U10.14 (CBUS3)
unnamed: R12.2, U10.7 (USBDM)
unnamed: R13.2, U10.6 (USBDP)
OUTN: R9.1, U1.10 (OUTN)
OUTP: R8.1, U1.11 (OUTP)
RX_ft: J4.2, U8.3 (PE1(TXD0)), U10.2 (RXD)
RefOut: R17.1, R18.2, R22.1, U7.6 (Vout)
Rel_In: C25.1, K3.6, R1.2, Rsns1.1
Rel_out: C1.1, C25.2, K3.5, U1.6 (INP)
Relay_ACDC: J7.3, R30.1, U8.78 (PA0(AD0))
TX_ft: J4.1, U8.2 (PE0(RXD0/PCINT8)), U10.15 (TXD)
VCCIO: C28.2, D5.2 (A), D6.2 (A), D7.2 (A), U10.1 (VCCIO), U10.8 (3V3OUT), U10.9 (~RESET)
Vocm: R22.2, R25.1, U5.2 (V_{OCM})
rst_an: R37.2, U4.2 (*RST), U11.4
rst_dn: C24.1, J1.1, J10.5, R28.1, SW1.2, U8.30 (~RESET), U11.2

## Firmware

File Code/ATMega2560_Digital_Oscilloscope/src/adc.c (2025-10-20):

#include "adc.h"
#include <avr/io.h>
#include <avr/interrupt.h>
#include <util/atomic.h>

/* ---------- Private state ---------- */
static volatile uint16_t s_result;
static volatile uint8_t  s_last_channel;
static volatile uint8_t  s_ready;           /* 0 = no new sample, 1 = new sample available */
static ADC_Callback      s_cb = 0;

/* ---------- Helpers ---------- */
static void adc_disable_digital_buffer(uint8_t channel) {
    if (channel < 8) {
        DIDR0 |= _BV(channel);          // ADC0D..ADC7D
    } else if (channel < 16) {
        DIDR2 |= _BV(channel - 8);      // ADC8D..ADC15D
    }
}

/* Map your GPIO_Pin (from gpio.h) to ADC channel (0..15).
 * On Mega: A0..A7 = PF0..PF7 => ADC0..ADC7; A8..A15 = PK0..PK7 => ADC8..ADC15. */
static int8_t adc_channel_from_pin(GPIO_Pin p) {
    if (p.port == &PORTF) return (int8_t)p.bit;          // 0..7
    if (p.port == &PORTK) return (int8_t)(8 + p.bit);    // 8..15
    return -1;
}

/* Select channel safely when ADC is idle. */
static inline void adc_select_channel(uint8_t channel) {
    if (channel & 0x08) ADCSRB |=  _BV(MUX5);  // channels 8..15
    else                ADCSRB &= ~_BV(MUX5);  // channels 0..7
    /* Keep REFS1:0 and ADLAR; set low 3 MUX bits (0..7 within bank). */
    ADMUX = (ADMUX & 0xE0) | (channel & 0x07);
}

/* ---------- Public API ---------- */
void ADC_set_reference(ADC_Reference ref) {
    /* Keep ADLAR=0 (right-adjust). Only change REFS1:0. */
    ADMUX = (ADMUX & ~(_BV(REFS1) | _BV(REFS0))) | ref;
    /* Note: first sample after changing Vref may be inaccurate. */
}

void ADC_init(ADC_Reference ref, uint8_t prescaler_bits) {
    /* Power up ADC clock domain. */
    PRR0 &= ~_BV(PRADC);

    /* Reference + right-adjust + clear MUX bits initially. */
    ADMUX  = (ref & (_BV(REFS1) | _BV(REFS0))); /* ADLAR=0 */
    ADCSRB = 0;                                 /* MUX5=0, ADTS=0 (no auto trigger) */

    /* Prescaler & enable; also enable interrupt (ADIE). */
    ADCSRA = _BV(ADEN) | _BV(ADIE) |
             (prescaler_bits & (_BV(ADPS2)|_BV(ADPS1)|_BV(ADPS0)));

    /* Clear any pending flag before first start. */
    ADCSRA |= _BV(ADIF);

    s_ready = 0;
}

bool ADC_start(uint8_t channel) {
    if (channel > 15) return false;

    /* If a conversion is ongoing, don't disturb ADMUX (datasheet: ADMUX is locked during conversion). */
    if (ADCSRA & _BV(ADSC)) return false;

    adc_disable_digital_buffer(channel);
    adc_select_channel(channel);

    s_last_channel = channel;
    s_ready = 0;

    /* Clear completion flag; then start single conversion. */
    ADCSRA |= _BV(ADIF);
    ADCSRA |= _BV(ADSC);
    return true;
}

bool ADC_start_pin(GPIO_Pin p) {
    int8_t ch = adc_channel_from_pin(p);
    if (ch < 0) return false;
    return ADC_start((uint8_t)ch);
}

bool ADC_busy(void) {
    return (ADCSRA & _BV(ADSC)) != 0;
}

bool ADC_result_ready(void) {
    return s_ready != 0;
}

bool ADC_get(uint16_t *out) {
    uint16_t v;
    uint8_t have = 0;

    ATOMIC_BLOCK(ATOMIC_RESTORESTATE) {
        if (s_ready) {
            v = s_result;
            s_ready = 0;         /* consume the sample */
            have = 1;
        }
    }

    if (have && out) *out = v;
    return (bool)have;
}

void ADC_set_callback(ADC_Callback cb) {
    ATOMIC_BLOCK(ATOMIC_RESTORESTATE) {
        s_cb = cb;
    }
}

/* ---------- Compatibility (blocking wrappers) ----------
 * These block until a fresh result arrives via the ISR.
 * REQUIREMENT: global interrupts must be enabled (sei()). */
uint16_t ADC_read(uint8_t channel) {
    while (!ADC_start(channel)) {
        /* Busy; wait for current conversion to finish. */
        /* If interrupts are disabled, this would deadlock — ensure sei() is used by the caller. */
    }
    while (!ADC_result_ready()) { /* wait for ISR to complete */ }
    uint16_t v = 0;
    (void)ADC_get(&v);
    return v;
}

uint16_t ADC_read_pin(GPIO_Pin p) {
    int8_t ch = adc_channel_from_pin(p);
    if (ch < 0) return 0xFFFFu;
    return ADC_read((uint8_t)ch);
}

/* ---------- ISR ---------- */
ISR(ADC_vect) {
    /* Read result (ADCL first, then ADCH). Using ADCW performs correct sequence. */
    uint16_t v = ADCW;

    s_result = v;
    s_ready  = 1;

    /* Clear interrupt flag explicitly (write 1 to ADIF). */
    ADCSRA |= _BV(ADIF);

    /* Optional user callback (keep it very short/ISR-safe). */
    if (s_cb) {
        s_cb(v, s_last_channel);
    }
}

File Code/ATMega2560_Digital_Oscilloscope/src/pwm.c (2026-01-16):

/*
 * pwm.c
 *
 * Implements a small HAL to control PWM channels on ATmega2560 (Arduino Mega mapping).
 *
 * Mapping used (Arduino Mega common mapping):
 * Timer0: OC0A = D13 (PB7), OC0B = D4 (PG5)
 * Timer1: OC1A = D11 (PB5), OC1B = D12 (PB6)
 * Timer2: OC2A = D10 (PB4), OC2B = D9  (PH6)
 * Timer3: OC3A = D5  (PE3), OC3B = D2  (PE4), OC3C = D3  (PE5)
 * Timer4: OC4A = D6  (PH3), OC4B = D7  (PH4), OC4C = D8  (PH5)
 * Timer5: RESERVED (used by millis/timekeeping); PWM on D44/D45/D46 disabled in this HAL
 *
 * This mapping follows Arduino Mega documentation and common pin mapping references. :contentReference[oaicite:1]{index=1}
 *
 * Note: timers 0 & 2 are 8-bit; timers 1,3,4,5 are 16-bit.
 *
 * Default behavior:
 * - Configure Fast PWM (8-bit for timers0/2, 16-bit for 1/3/4/5 using ICRn = 0xFFFF).
 * - Non-inverting mode.
 * - Prescaler default = 64 (common Arduino-ish value).
 *
 * Changing prescaler/mode will affect all pins sharing the same timer.
 */

#include "pwm.h"
#include <avr/io.h>
#include <avr/interrupt.h>
#include <string.h>

/* Internal helper: return timer id (0..5) and channel ('A'/'B'/'C') or -1 if not PWM pin */
typedef struct
{
    int8_t timer; /* 0..5, or -1 if not PWM */
    char ch;      /* 'A','B','C' */
} pwm_map_t;

static pwm_map_t pwm_map_from_pin(GPIO_Pin p);

/* Return counter width: 8 or 16 */
static uint8_t pwm_timer_width(int8_t timer_id)
{
    if (timer_id == 0 || timer_id == 2)
        return 8;
    if (timer_id >= 1 && timer_id <= 5)
        return 16;
    return 0;
}

/* Top for 16-bit timers (we set ICRn = 0xFFFF in init by default) */
static uint32_t pwm_default_top(int8_t timer_id)
{
    if (pwm_timer_width(timer_id) == 8)
        return 0xFFu;
    switch (timer_id)
    {
    case 1:
        return ICR1;
    case 3:
        return ICR3;
    case 4:
        return ICR4;
    default:
        return 0; // should not happen
    }
}

/* Public API */

void PWM_init(void)
{
    cli();

    /* Timer0: Fast PWM, 8-bit (WGM01:0 = 3) -> WGM02 in TCCR0B = 0 => mode 3 (fast 8-bit)
     * Set COM0A1:0 and COM0B1:0 later in attach
     * Prescaler: set CS02:0 = prescaler 64 -> CS02=0,CS01=1,CS00=1
     */
    TCCR0A = (1 << WGM00) | (1 << WGM01);
    TCCR0B = (1 << CS01) | (1 << CS00); /* prescaler 64 */

    /* Timer2: Fast PWM, 8-bit (WGM21:0 = 3), prescaler 64 */
    TCCR2A = (1 << WGM20) | (1 << WGM21);
    TCCR2B = (1 << CS22); /* CS22:0 = 100 => prescaler 64 on many setups (check datasheet) */
    /* Note: some chips use different CS bits—this is the common Arduino choice for Timer2 */

    /* Timer1,3,4,5: Configure for Fast PWM, mode 14 (WGMn3:0 = 14) where TOP = ICRn.
     * That requires setting WGMn bits across TCCRnA and TCCRnB. We'll set ICRn = 0x00FF
     * (8-bit TOP) to get ~200 Hz at 16 MHz with prescaler 64, which avoids visible flicker
     * on LEDs while keeping simple scaling. Prescaler = 64 (CSn2..0).
     */
    /* Timer1 */
    TCCR1A = (1 << WGM11);
    TCCR1B = (1 << WGM13) | (1 << WGM12) | (1 << CS11) | (1 << CS10); /* presc 64 */
    // ICR1 = 0x00FF;
    ICR1 = 0x04EF; // 200Hz

    /* Timer3 */
    TCCR3A = (1 << WGM31);
    TCCR3B = (1 << WGM33) | (1 << WGM32) | (1 << CS31) | (1 << CS30);
    ICR3 = 0x00FF;

    /* Timer4 */
    TCCR4A = (1 << WGM41);
    TCCR4B = (1 << WGM43) | (1 << WGM42) | (1 << CS41) | (1 << CS40);
    ICR4 = 0x00FF;

    /* Timer5 intentionally left unconfigured (reserved for timekeeping) */

    sei();
}

/* Internal: enable compare output for a (timer,channel) in non-inverting mode */
static void enable_compare_output(int8_t timer, char ch)
{
    switch (timer)
    {
    case 0:
        if (ch == 'A')
            TCCR0A |= (1 << COM0A1);
        else if (ch == 'B')
            TCCR0A |= (1 << COM0B1);
        break;
    case 1:
        if (ch == 'A')
            TCCR1A |= (1 << COM1A1);
        else if (ch == 'B')
            TCCR1A |= (1 << COM1B1);
        else if (ch == 'C')
            TCCR1A |= (1 << COM1C1);
        break;
    case 2:
        if (ch == 'A')
            TCCR2A |= (1 << COM2A1);
        else if (ch == 'B')
            TCCR2A |= (1 << COM2B1);
        break;
    case 3:
        if (ch == 'A')
            TCCR3A |= (1 << COM3A1);
        else if (ch == 'B')
            TCCR3A |= (1 << COM3B1);
        else if (ch == 'C')
            TCCR3A |= (1 << COM3C1);
        break;
    case 4:
        if (ch == 'A')
            TCCR4A |= (1 << COM4A1);
        else if (ch == 'B')
            TCCR4A |= (1 << COM4B1);
        else if (ch == 'C')
            TCCR4A |= (1 << COM4C1);
        break;
        /* Timer5 reserved: no PWM enable */
    }
}

/* Internal: disable compare output for (timer,channel) */
static void disable_compare_output(int8_t timer, char ch)
{
    switch (timer)
    {
    case 0:
        if (ch == 'A')
            TCCR0A &= ~((1 << COM0A1) | (1 << COM0A0));
        else if (ch == 'B')
            TCCR0A &= ~((1 << COM0B1) | (1 << COM0B0));
        break;
    case 1:
        if (ch == 'A')
            TCCR1A &= ~((1 << COM1A1) | (1 << COM1A0));
        else if (ch == 'B')
            TCCR1A &= ~((1 << COM1B1) | (1 << COM1B0));
        else if (ch == 'C')
            TCCR1A &= ~((1 << COM1C1) | (1 << COM1C0));
        break;
    case 2:
        if (ch == 'A')
            TCCR2A &= ~((1 << COM2A1) | (1 << COM2A0));
        else if (ch == 'B')
            TCCR2A &= ~((1 << COM2B1) | (1 << COM2B0));
        break;
    case 3:
        if (ch == 'A')
            TCCR3A &= ~((1 << COM3A1) | (1 << COM3A0));
        else if (ch == 'B')
            TCCR3A &= ~((1 << COM3B1) | (1 << COM3B0));
        else if (ch == 'C')
            TCCR3A &= ~((1 << COM3C1) | (1 << COM3C0));
        break;
    case 4:
        if (ch == 'A')
            TCCR4A &= ~((1 << COM4A1) | (1 << COM4A0));
        else if (ch == 'B')
            TCCR4A &= ~((1 << COM4B1) | (1 << COM4B0));
        else if (ch == 'C')
            TCCR4A &= ~((1 << COM4C1) | (1 << COM4C0));
        break;
        /* Timer5 reserved: no PWM disable needed */
    }
}

int PWM_attach(GPIO_Pin p)
{
    pwm_map_t m = pwm_map_from_pin(p);
    if (m.timer < 0)
        return -1;

    /* configure pin as output */
    GPIO_set_output(p);

    /* enable compare output in non-inverting mode */
    enable_compare_output(m.timer, m.ch);

    return 0;
}

int PWM_detach(GPIO_Pin p)
{
    pwm_map_t m = pwm_map_from_pin(p);
    if (m.timer < 0)
        return -1;

    disable_compare_output(m.timer, m.ch);
    return 0;
}

/* Write raw duty (scaled by width) */
int PWM_write_raw(GPIO_Pin p, uint32_t value)
{
    pwm_map_t m = pwm_map_from_pin(p);
    if (m.timer < 0)
        return -1;

    uint8_t width = pwm_timer_width(m.timer);

    if (width == 8)
    {
        uint8_t v = (value > 0xFFu) ? 0xFFu : (uint8_t)value;
        switch (m.timer)
        {
        case 0:
            if (m.ch == 'A')
                OCR0A = v;
            else
                OCR0B = v;
            break;
        case 2:
            if (m.ch == 'A')
                OCR2A = v;
            else
                OCR2B = v;
            break;
        }
    }
    else
    {
        uint16_t top = (uint16_t)pwm_default_top(m.timer);
        uint16_t v = (value > top) ? top : (uint16_t)value;
        switch (m.timer)
        {
        case 1:
            if (m.ch == 'A')
                OCR1A = v;
            else if (m.ch == 'B')
                OCR1B = v;
            else
                OCR1C = v;
            break;
        case 3:
            if (m.ch == 'A')
                OCR3A = v;
            else if (m.ch == 'B')
                OCR3B = v;
            else
                OCR3C = v;
            break;
        case 4:
            if (m.ch == 'A')
                OCR4A = v;
            else if (m.ch == 'B')
                OCR4B = v;
            else
                OCR4C = v;
            break;
            /* Timer5 reserved: no OCR writes */
        }
    }
    return 0;
}

int PWM_write_percent(GPIO_Pin p, float percent)
{
    if (percent < 0.0f)
        percent = 0.0f;
    if (percent > 100.0f)
        percent = 100.0f;
    pwm_map_t m = pwm_map_from_pin(p);
    if (m.timer < 0)
        return -1;
    uint32_t maxv = pwm_default_top(m.timer);
    uint32_t val = (uint32_t)((percent / 100.0f) * (float)maxv + 0.5f);
    return PWM_write_raw(p, val);
}

uint32_t PWM_get_max(GPIO_Pin p)
{
    pwm_map_t m = pwm_map_from_pin(p);
    if (m.timer < 0)
        return 0;
    return pwm_default_top(m.timer);
}
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

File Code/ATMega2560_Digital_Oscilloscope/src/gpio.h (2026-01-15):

#ifndef GPIO_H
#define GPIO_H

#include <avr/io.h>
#include <stdint.h>

typedef struct
{
    volatile uint8_t *ddr;
    volatile uint8_t *port;
    volatile uint8_t *pinReg;
    uint8_t bit;
} GPIO_Pin;

static void GPIO_set_output(GPIO_Pin p) { *(p.ddr) |= _BV(p.bit); }
static void GPIO_set_input(GPIO_Pin p) { *(p.ddr) &= ~_BV(p.bit); }
static void GPIO_set_high(GPIO_Pin p) { *(p.port) |= _BV(p.bit); }
static void GPIO_set_low(GPIO_Pin p) { *(p.port) &= ~_BV(p.bit); }
static void GPIO_toggle(GPIO_Pin p) { *(p.port) ^= _BV(p.bit); }
static uint8_t GPIO_read(GPIO_Pin p) { return (*(p.pinReg) & _BV(p.bit)) != 0; }

#define GPIO_PIN(L, N) ((GPIO_Pin){&DDR##L, &PORT##L, &PIN##L, P##L##N})

// Pin definitions for Arduino Mega 2560
#define ONBOARD_LED GPIO_PIN(B, 7)

#define D0 GPIO_PIN(E, 0)  // USART0_RX
#define D1 GPIO_PIN(E, 1)  // USART0_TX
#define D2 GPIO_PIN(E, 4)  // PWM2
#define D3 GPIO_PIN(E, 5)  // PWM3
#define D4 GPIO_PIN(G, 5)  // PWM4
#define D5 GPIO_PIN(E, 3)  // PWM5
#define D6 GPIO_PIN(H, 3)  // PWM6
#define D7 GPIO_PIN(H, 4)  // PWM7
#define D8 GPIO_PIN(H, 5)  // PWM8
#define D9 GPIO_PIN(H, 6)  // PWM9
#define D10 GPIO_PIN(B, 4) // PWM10
#define D11 GPIO_PIN(B, 5) // PWM11
#define D12 GPIO_PIN(B, 6) // PWM12
#define D13 GPIO_PIN(B, 7) // PWM13 / LED
#define D14 GPIO_PIN(J, 1) // USART3_TX
#define D15 GPIO_PIN(J, 0) // USART3_RX
#define D16 GPIO_PIN(H, 1) // USART2_TX
#define D17 GPIO_PIN(H, 0) // USART2_RX
#define D18 GPIO_PIN(D, 3) // USART1_TX
#define D19 GPIO_PIN(D, 2) // USART1_RX
#define D20 GPIO_PIN(D, 1) // I2C_SDA
#define D21 GPIO_PIN(D, 0) // I2C_SCL

#define D22 GPIO_PIN(A, 0)
#define D23 GPIO_PIN(A, 1)
#define D24 GPIO_PIN(A, 2)
#define D25 GPIO_PIN(A, 3)
#define D26 GPIO_PIN(A, 4)
#define D27 GPIO_PIN(A, 5)
#define D28 GPIO_PIN(A, 6)
#define D29 GPIO_PIN(A, 7)

#define D30 GPIO_PIN(C, 7)
#define D31 GPIO_PIN(C, 6)
#define D32 GPIO_PIN(C, 5)
#define D33 GPIO_PIN(C, 4)
#define D34 GPIO_PIN(C, 3)
#define D35 GPIO_PIN(C, 2)
#define D36 GPIO_PIN(C, 1)
#define D37 GPIO_PIN(C, 0)
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

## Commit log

2025-10-16 Revise output details and add project development steps
    Updated output specification and added project stages.
2025-10-23 Added preliminary components list and Hardware design timeline
    [Circuit_Design_DO.kicad_pcb, Circuit_Design_DO.kicad_sch]
2025-10-25 Components Excel sheet
    Added Excel sheet for components alongside prices and links
    [Componente.xlsx]
2025-10-30 Added new folder for components and initial commit of schematic work
    [Circuit_Design_DO.kicad_sch]
2025-10-30 Renamed Componenete.xlsx to Components.xlsx and updated Components.txt
    [Components.xlsx]
2025-10-30 Renamed folder Extra_components to Components and moved all related files in it, added datasheets
    [Components.xlsx]
2025-11-03 Updated SS pin
    Keep Slave Select in 1 so board stays in Master mode
2025-12-04 Updated schematic design (missing some headers for now), started layout design
    [Circuit_Design_DO.kicad_pcb]
2025-12-10 Added a folder for a normal pcb design, the other one is Arduino style, started an Arduino PCB layout with headers, repaired schematic mistakes
    [Circuit_Design_DO.kicad_pcb, Circuit_Design_DO.kicad_sch]
2025-12-13 Outlined layout for non-Arduino PCB, started to place components
    [Circuit_Design_DO.kicad_pcb, Circuit_Design_DO.kicad_sch]
2025-12-13 Power circuits and microcontroller+oscillator placement
    [Circuit_Design_DO.kicad_pcb]
2025-12-14 Added frontend circuits, powerplanes, changed relay component
    [Circuit_Design_DO.kicad_pcb, Circuit_Design_DO.kicad_sch]
2025-12-29 Almost done PCB design and final hardware checks
    [Circuit_Design_DO.kicad_pcb, Circuit_Design_DO.kicad_sch, freerouting.dsn, temp-freerouting.dsn]
2025-12-29 Finished PCB and electronic design
    [Circuit_Design_DO-B_Cu.gbr, Circuit_Design_DO-B_Mask.gbr, Circuit_Design_DO-B_Paste.gbr, Circuit_Design_DO-B_Silkscreen.gbr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]
2025-12-29 Final touches
    [Circuit_Design_DO-B_Cu.gbr, Circuit_Design_DO-B_Mask.gbr, Circuit_Design_DO-B_Paste.gbr, Circuit_Design_DO-B_Silkscreen.gbr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]
2025-12-29 Update Cablaj status and add PCB assembly note
2026-01-14 added Doc template
    [Circuit_Design_DO.kicad_pcb, bom_updated.xls]
2026-01-15 Added slides file
    [Circuit_Design_DO.kicad_sch]
2026-03-25 removed secondary design
    [Circuit_Design_DO.kicad_pcb, Circuit_Design_DO.kicad_sch]
